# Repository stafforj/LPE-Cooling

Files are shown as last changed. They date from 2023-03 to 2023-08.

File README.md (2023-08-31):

# Liquid Exfoliation Cooling System

_A low-cost approach for cooling high shear exfoliation and material blending processes. The main cooling apparatus is constructed from 3D-printed components and off-the-shelf pipe connectors. Included are the designs and build notes. Part of the Open Science Framework repository [OpenLPE](https://osf.io/evupy/)._

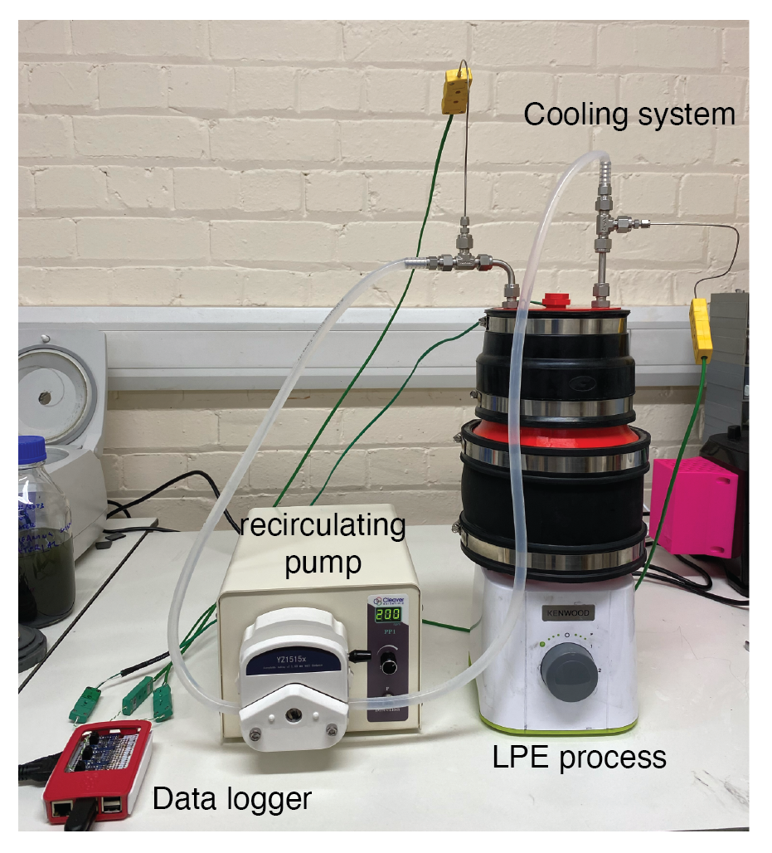
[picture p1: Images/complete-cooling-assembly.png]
Complete LPE assembly


## Background & Motivation

_This is part of the [OpenLPE](https://osf.io/evupy/) labware project._

High shear exfoliation is a process that uses mechanical force to produce atomically thin materials in liquid dispersions. Our research explores and utilises these processes to synthesise materials such as graphene, graphene-based materials, and others including transition metal dichalcogenides. We decided to create a low-cost, controllable shear exfoliation system that would be capable of synthesising reasonable product concentrations and formulating functional inks/composites at laboratory scales (~ 100 mL volumes). The aim was to design and build a scientific instrument which would allow researchers to do this with a low entry cost (~ 200 GBP). 

Standard kitchen blenders have previously been proven capable of performing high shear exfoliation of two-dimensional materials [[doi:10.1039/C4NR03560G](https://doi.org/10.1039/C4NR03560G), [doi:10.1016/j.carbon.2014.07.035](https://doi.org/10.1016/j.carbon.2014.07.035)]. Recently, our group has extended this accessible technique to include _in situ_ spectroscopy [[doi:10.1016/j.cherd.2021.10.041](https://doi.org/10.1016/j.cherd.2021.10.041)] and up-cycling of electric vehicle battery anodes at end-of-life [[doi:10.1021/acs.iecr.2c02634](https://doi.org/10.1021/acs.iecr.2c02634)]. High shear exfoliation processes tend to generate viscous heating which can increase product temperature significantly above ambient. For many applications and research investigations, it can be necessary to control these process temperatures (e.g., for chemical reactions or to avoid solvent evaporation).   

This repository provides the build details and CAD for creating a cooling system that can control the temperature of a liquid exfoliation process. These are designed around a high shear exfoliation process which utilises a controllable kitchen blender to impart a range of shear rates ($\dot{\gamma} \sim 10^2-10^5$ s $^{-1}$). We provide build details on how to modify and integrate programmable control of a kitchen blender here: [PID-Blender](https://github.com/DTP587/PID-Blender). Some of the CAD files are designed for this specific blender vessel (Kenwood BLP31.D0WG), however, the approach and configuration is extendable to any vessel and our CAD files and instructions can be used as templates to work from in these circumstances.

Below shows the recovery of few-layer graphene in aqueous-surfactant dispersions (De-ionised water / Sodium Cholate) that were produced using this cooled high shear exfoliation device.

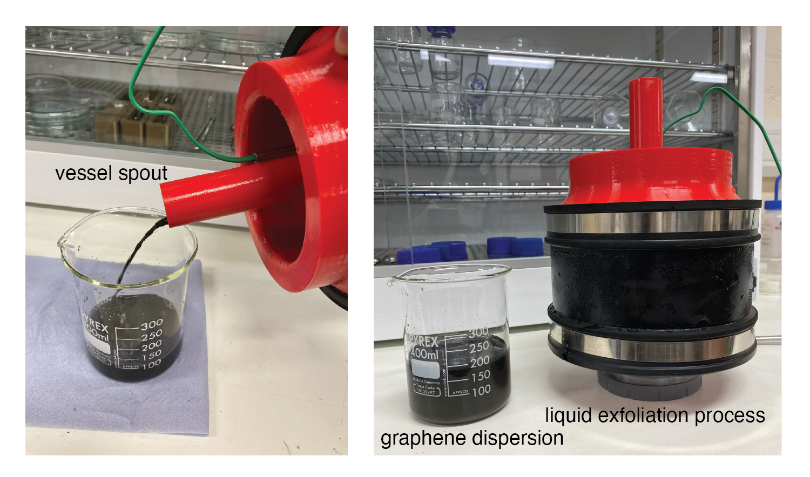
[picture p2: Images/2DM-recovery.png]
Production of FLG


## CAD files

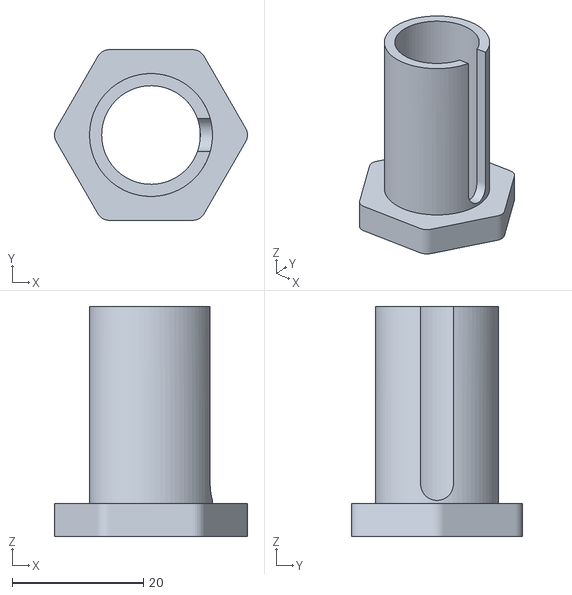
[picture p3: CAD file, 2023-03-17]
CAD/VesselCooler-TC-port.stl
29.4 x 26.0 x 35.0

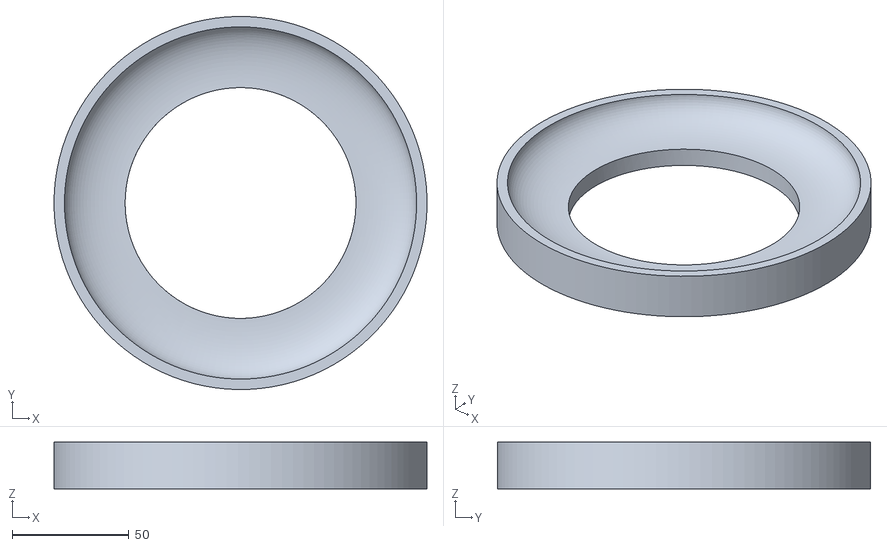
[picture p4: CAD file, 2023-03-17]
CAD/VesselCooler-Base.stl
160.0 x 160.0 x 20.0

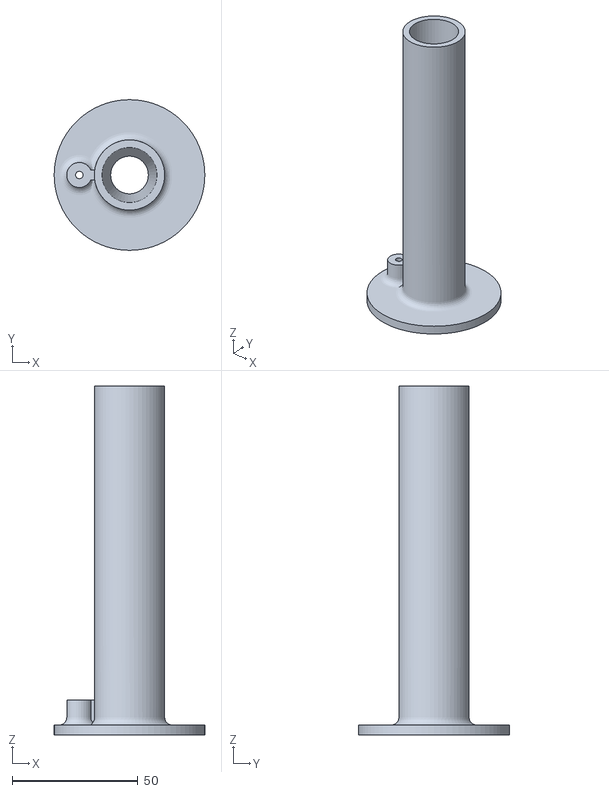
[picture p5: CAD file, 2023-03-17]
CAD/VesselCooler-chimney.stl
60.0 x 60.0 x 139.0

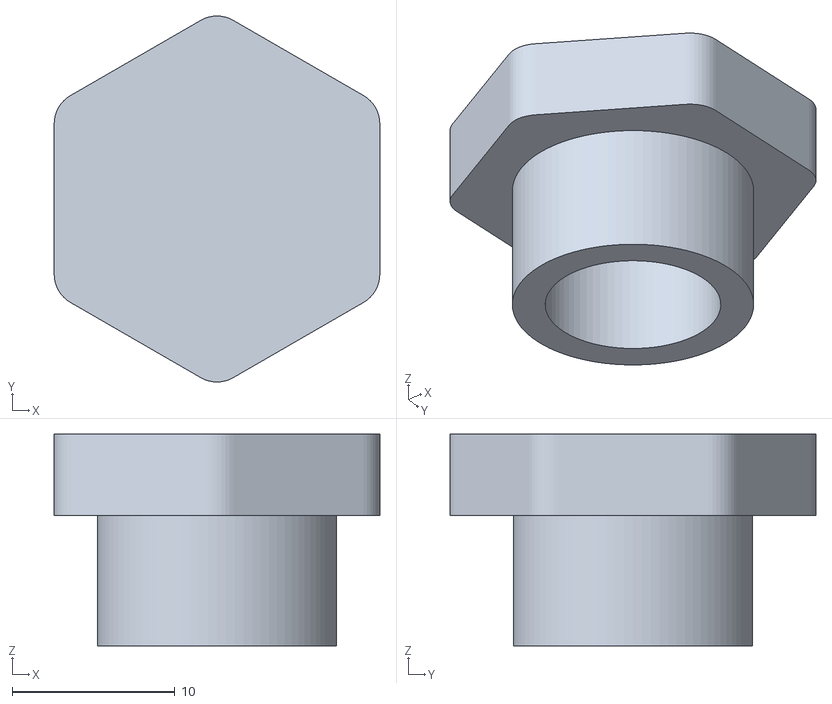
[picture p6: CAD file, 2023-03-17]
CAD/VesselCooler-TC-port-plug.stl
20.0 x 22.5 x 13.0

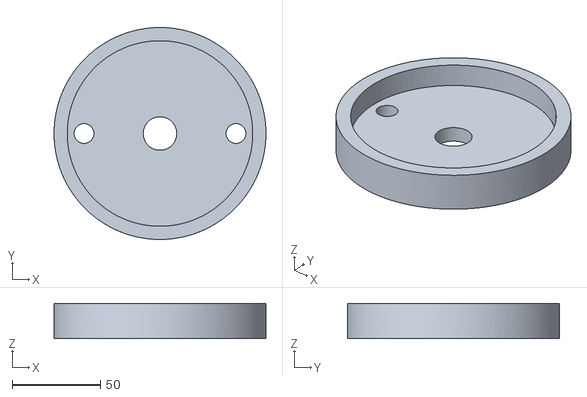
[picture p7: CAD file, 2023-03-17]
CAD/VesselCooler-Top.stl
120.0 x 120.0 x 20.0

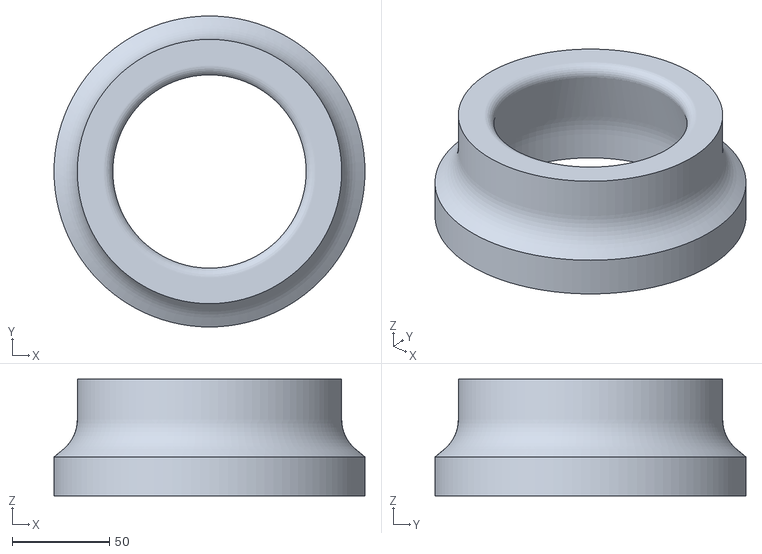
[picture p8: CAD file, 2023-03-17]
CAD/VesselCooler-Middle.stl
160.0 x 160.0 x 60.0

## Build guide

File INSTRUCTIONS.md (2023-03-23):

# Build Instructions and Notes

### Operating Principles

Liquid exfoliation processes, and many other mixing/formulation operations, impart high shear rates ($\dot{\gamma}$) on precursor materials dispersed in solvents. This action can generate heat through viscous heating of the fluid ($\dot{Q}$). A schematic of a liquid exfoliation process that uses a rapidly rotating impeller inside a closed vessel filled with solvent and precursor materials is shown in the schematic below. When the vessel is allowed to cool naturally in air, the amount of heat that can be dissipated from the system is limited by passive heat transfer modes from the external surface of the vessel to the ambient surroundings (natural convection & radiation, $Q_{nc}''$). This can result in uncontrollable and high product temperatures that can affect the mixing process if there is a sensitivity to temperature, and/or impact the reliability of the exfoliation system itself (thermo-mechanical failures).

The aim of this build is to provide a low-cost approach that can cool a kitchen blender vessel during the liquid exfoliation of nanomaterials. The operating principle of the cooling system is illustrated on the right in the schematic below. A cooling jacket surrounds the process vessel. The internal space is filled with ice cubes and chilled water which removes thermal energy from the process vessel using two heat transfer modes - the latent heat of fusion from a phase change of ice ($Q_{pc}''$) and the sensible heating of liquid water that is enhanced by coolant recirculation ($Q_{cv}''$).

This build can be combined with the following repositories to create a standalone, low-cost scientific apparatus with speed and temperature control: 

1. [Thermocouple-Datalogger](https://github.com/stafforj/Thermocouple-Datalogger) repository for temperature data aquisition module.
2. [PID-blender](https://github.com/DTP587/PID-Blender) repository for finely tuned blender speed control, or
3. [Automated-Relay-Switch](https://github.com/stafforj/Automated-Relay-Switch) repository for basic blender control.

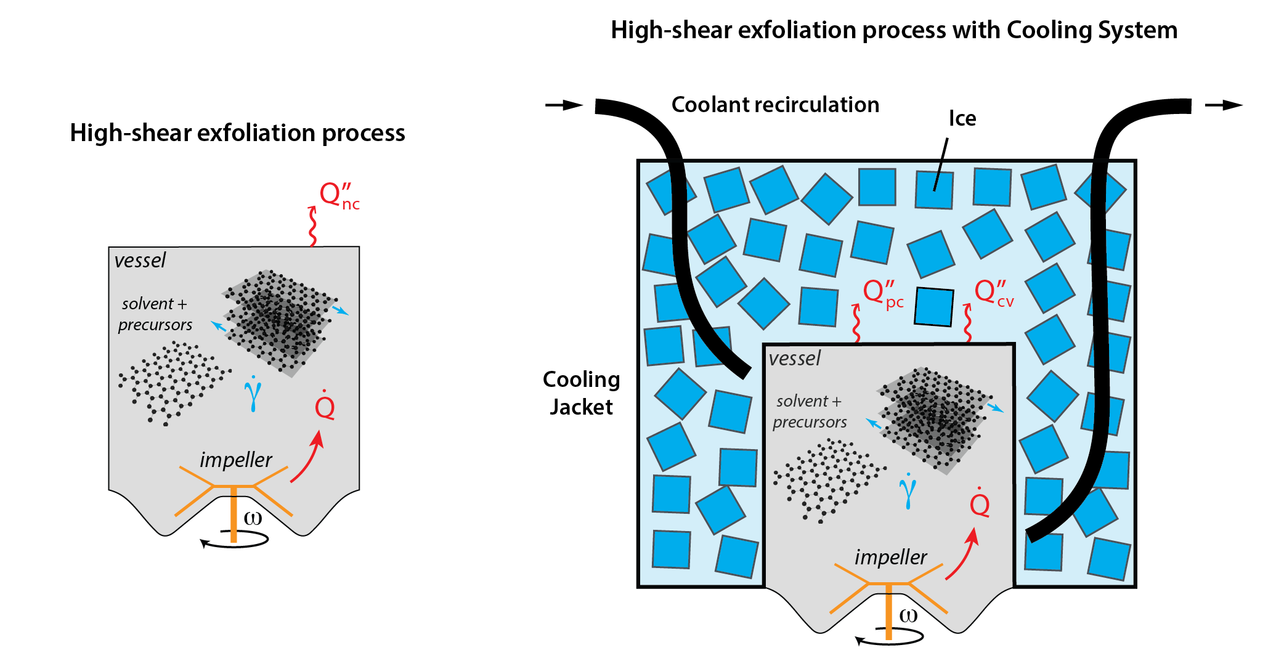
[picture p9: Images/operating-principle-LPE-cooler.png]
Operating principle


## Bill of Materials

The BoM is split into the main components for the cooling system and additional components that are optional. These additional parts facilitate coolant recirculation, or if using an external chiller to provide the cooling function instead of ice. The optional components listed below add greater cost to the build (relative to the main component costs). This cost can be reduced by moving to other types of fittings and tubing (e.g., brass fittings and copper tubing).

### Main items

|Name               |QTY|Description                           |
|:------------------|:-:|:-------------------------------------|
|PETG|1  |PETG filament for 3D-printing. 386 grams used to print all components. |
|[Silicon conformal sealant](https://uk.rs-online.com/web/p/conformal-coatings/1247695)|1 |Silicon conformal spray coating. Approximately 100 mL used.|
|[EPDM Pipe Adaptor (1)](https://www.screwfix.com/p/floplast-flexi-adaptor-160mm/1009v)|1  |Flexible EPDM pipe adaptor 160mm.|
|[EPDM Pipe Adaptor (2)](https://www.screwfix.com/p/floplast-underground-flexible-adaptor-120-136mm/19914)|1  |Flexible EPDM pipe adaptor 120-136mm.|
|[Adhesive/Sealant](https://www.screwfix.com/p/soudal-fix-all-high-tack-adhesive-sealant-white-290ml/64585)|1  |High bond strength adhesive/sealant. Approximately 30 mL used.|
|[Thermocouple](https://www.tcdirect.co.uk/product-2-190-1---Mineral-Insulated-Thermocouple-with-Pot-Seal-0-25-0-5-0-75-1-0-1-5-and-3-0mm-diameters)|1  |Type K thermocouple with 3 mm 310 SS probe sheath diameter, 100 mm length.|
|Bag of ice|1  |2 kg bag of ice cubes.|
|Thermocouple reader|1 |Data logger for reading Type K thermocouples. See our [Thermocouple-Datalogger](https://github.com/stafforj/Thermocouple-Datalogger) build for a RPi-based datalogger.
|Kitchen blender |1 |Standard off-the-shelf, [relay-controlled](https://github.com/stafforj/Automated-Relay-Switch), or [PID-controlled](https://github.com/DTP587/PID-Blender).
|[Funnel](https://www.fishersci.co.uk/shop/products/borosilicate-glass-powder-funnel-9/12993591?emb_id=pp_euorderconfirmation_producttitle) |1 |Glass/Plastic funnel for precursor loading. 70mm diameter (top), 16mm diameter (stem), 25 mm length.
|Misc.|   | <ul><li>Spanners</li><li>Screwdrivers</li><li>Gloves</li><li>Face mask</li><li>Electrical drill/Rotary tool</li><li>1L water</li></ul>|

### Coolant recirculation (optional)

|Name               |QTY|Description                           |
|:------------------|:-:|:-------------------------------------|
|SS tube|1  |1/4" stainless steel tube. 300mm length used. |
|[SS Bulkhead Union](https://buy.ham-let.com/774lss1-4)|2  |Bulk head fittings mounted to top 3D-printed part.|
|[SS Tube stub adapter](https://buy.ham-let.com/130ltss1-4x1-4)|2  |1/4" Hose barb fitting.|
|[SS Union Tee](https://buy.ham-let.com/764lss1-4)|2  |1/4" Tee fitting.|
|[SS Reducer](https://buy.ham-let.com/767ltss1-16x1-4tc)|2  |1/16" to 1/4" tube fitting.|
|[Thermocouple](https://uk.rs-online.com/web/p/thermocouples/3971501)|2  |Type K thermocouple with 1.5mm SS probe sheath diameter, 150mm length.|
|Tubing|1  |Silicon or Tygon tubing or similiar. 3m length used, 6mm or 1/4" ID. |
|Pump|1  |Pump of choice to recirculate coolant. |
|Misc.|   | <ul><li>Spanners</li><li>Screwdrivers</li><li>Pipe bender</li></ul>|

## Design & Construction

### Thermal Design

The hardware design is based on the thermal loads that need to be dissipated from the liquid exfoliation system. For this build we use a 350 W Kenwood BLP31.D0WG blender. We typically operate the process for $t ≈ 15$ mins to perform a synthesis [[doi:10.1021/acs.iecr.2c02634](https://doi.org/10.1021/acs.iecr.2c02634)]. Next, we can estimate the amount of ice that would melt into liquid water using the latent heat of fusion.

```
Heat load: 350 W = 350 J/s = 21 kJ/min
Latent heat of fusion = 334 kJ/kg

21kJ/min / 334kJ/kg = 0.063 kg/min
1260kJ/h / 334kJ/kg = 3.77 kg/h
```
Which shows that ≈ 1 kg of ice can melt in 15 mins. This is a basic starting point for sizing the cooling jacket. For this application, the design must be capable of holding 1 kg of ice around the vessel at a minimum. Ideally, it should be made bigger than this to accommodate the simplified assumptions that have been made, secondary heat loss/gain, as well as accounting for any future requirements such as longer process times.

Adding ice cubes to the cooling jacket leaves air gaps that have a negligible contribution to the heat transfer from the vessel. The complete surface of the heated process vessel also won't be in direct contact with the ice due to these voids. Filling and recirculating chilled water (e.g., $T$ ≈ 0.1-1°C) can remove these insulative air gaps with a liquid coolant and promote uniform cooling over the entire vessel surface (see previous schematic). If the jacket is filled with an additional 1 L of chilled water, the sensible heating contribution assuming a target temperature rise of 10°C can be calculated as:

```
m: mass of chilled water (1kg) + mass of melt water (1kg)
Cp: specific heat capacity
DT: temperature rise

Q_s = m*Cp*DT = 2*4184*10 = 83.7 kJ
```

Although this is a useful cooling contribution, it also illustrates the importance of phase change heat transfer to the cooling process (recall the value for latent heat of fusion). A jacket size of 2.6 L was chosen to meet the material processing requirements. This provided a volume ≈ 25% greater than the 2.1 L that this simple analysis was based on (1kg ice + 1L water).

Additionally, as the jacket temperature is lower than the ambient air outside ($T_{amb}$ ≈ 20°C in the lab), heat is gained by the cooling system. We can calculate this assuming a heat transfer coefficient of $h = 7.5$ W/m $^2$ K, representing an average of the typical range of $h$ for natural convection (~ 5-10 W/m $^2$ K). Taking a cooling jacket diameter of 170 mm and height of 250 mm, the heat gained from the ambient, $Q_g$ is:

```
h: heat transfer coefficient
A: external surface area of the cooling jacket
DT: temperature difference between the ambient air and cooling jacket

Q_g = h*A*DT = 7.5*(2*pi*0.085*0.250)*20 = 20 W
20 W = 20 J/s =  1.2 kJ/min
```
This assumes the external surface is not insulated. Wrapping the cooling jacket with insulation can reduce some of the heat gain to the jacket. The final estimates accounting for $Q_s$ and $Q_g$ are:

```
Energy from latent heat of fusion: 334 kJ
Energy from heating 2 kg water by 10°C: 83.7 kJ
Total energy = 417.7 kJ to heat the ice/water jacket mixture by 10°C

Heat generation from LPE process: 21 kJ/min
Ambient heat gain: 1.2 kJ/min
Total heat rate = 22.2 kJ/min (heat added to ice/water jacket)

Total processing time before the coolant temperature reaches 10°C
t = 417.7 / 22.2 = 18.8 min
```
This provides sufficient flexibility to facilitate cooling for a target process time of $t = 15$ mins. Note that this only considers heat loads during the process "ON" time. If the process is run intermittently (e.g., 1 minute ON, 1 minute OFF, etc.), the ambient heat gain persists during the process OFF time. A revised estimate of the cooling time should be calculated with these considerations.

### CAD files

A total of six components from the cooling system are 3D-printed parts. The CAD (.stl) files for printing these parts are located within the folder `./CAD/`.

### Construction

The CAD files were printed using a fused-deposition-modeling (FDM) printer (Ultimaker S3, 0.2mm layer thickness, 20\% infill, no supports). Polyethylene terephthalate glycol (PETG) was selected as the filament material for the printing process due to its ability to tolerate high temperatures (~ 70-80°C), its mechanical properties, printability, and chemical resistance to certain oils and solvents. 

In this build, the components are exposed to water and ice. Although PETG is compatible with water, the layers resulting from the FDM process can create sites for fluid leakages in the finished part. To remove the risk of leaks, the 3D-printed parts were coated with a thin film silicon-based conformal coating (~ 100 microns thickness). To show the visual effect of this coating, a sample part was 3D-printed and masked with tape to partially cover it with a single spray coat (~ 25 microns). The difference between the coated and uncoated PETG surface is shown in the image below. The conformal coating covers the layers and insterstices, sealing the printed part and preventing liquid leaks. This surface coating is mechanically robust. As the surfaces in contact with the coolant and product are a different material than PETG, the chemical resistance of coated parts should be re-assessed for applications where a coolant other than water/ice is used. The spray coating should be performed in a well-ventilated environment and wearing the appropriate PPE.   

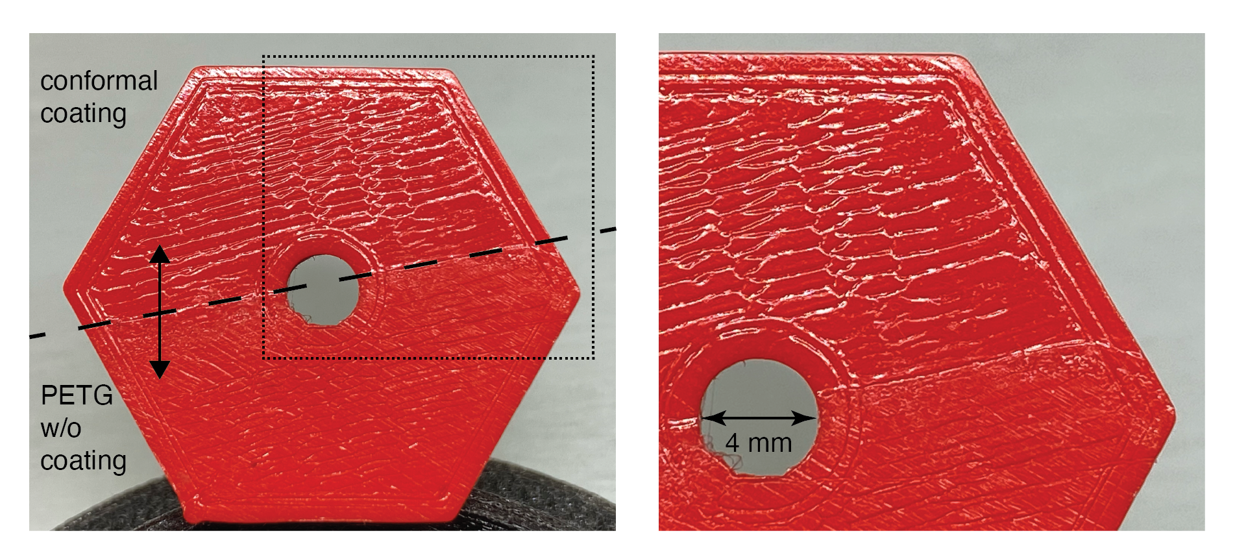
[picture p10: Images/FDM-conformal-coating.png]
Conformal coating


Once printed, the parts were coated with three spray coats and allowed to cure at room temperature (~ 20°C) for 24 hours between coatings. The components of the cooling system are shown in the image below.

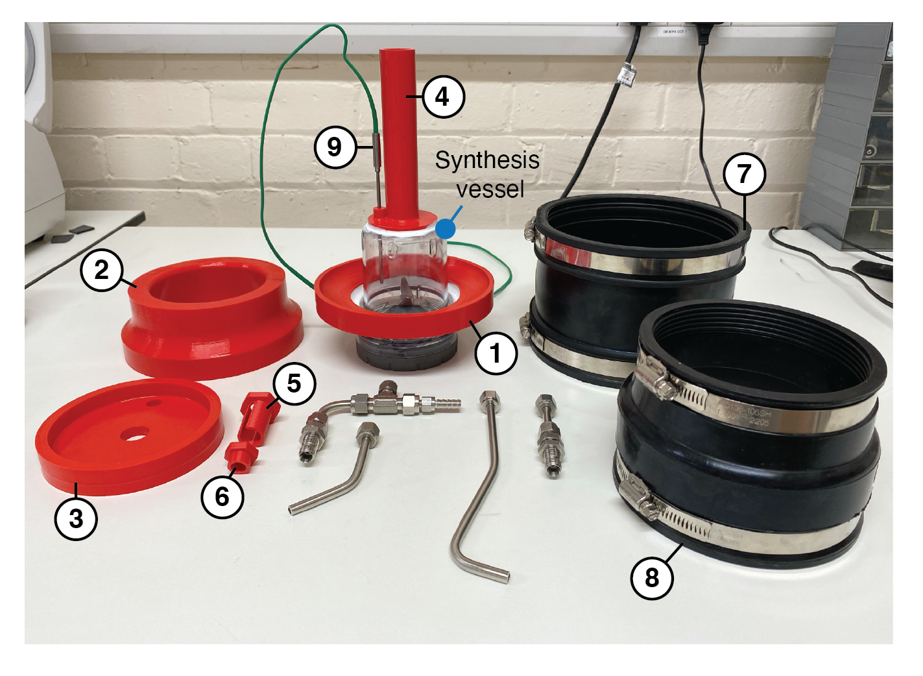
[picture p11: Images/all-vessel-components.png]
Component breakdown


Components `1`, `4` and `9` were bonded to the synthesis vessel (Kenwood BLP31.D0WG) using a sealant adhesive. The spout with integrated thermocouple mounting (Component `4`), required modifications to the synthesis vessel before the bonding process. A 15 mm diameter hole was drilled at the top and centre of the vessel. This hole allows filling the vessel with precursor materials from the top (shown later). A second 4 mm diameter hole, located 20 mm from the centre of the vessel, was drilled to accomodate the insertion of a thermocouple probe for measuring the process temperature. The thermocouple probe is inserted into component `4` at the desired depth, and the part then bonded to the top of the vessel. 

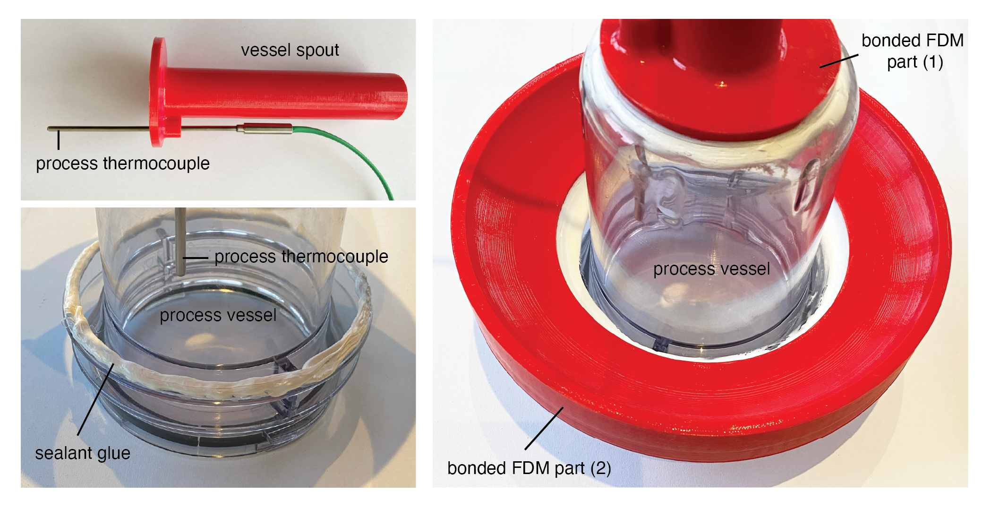
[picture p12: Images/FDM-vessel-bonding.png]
Bonding construction


The complete assembly instructions are discussed in the following sections. The following image shows the barebone assembly of printed parts and synthesis vessel without the cooling jacket installed. The vessel spout was also designed to facilitate product sampling during material processing. Here, you can see a 10 mL pipette inserted into the vessel through the opening in the top part. Product samples can be taken without dissassembling the vessel, or interfering with the thermocouple or cooling system itself. The (optional) coolant recirculation pipes were formed using SS tubing and a pipe bender. These are intended to transport cooling fluid onto and away from the synthesis vessel, improving the convective heat transport from the external walls of the vessel ($Q_{cv}"$).        

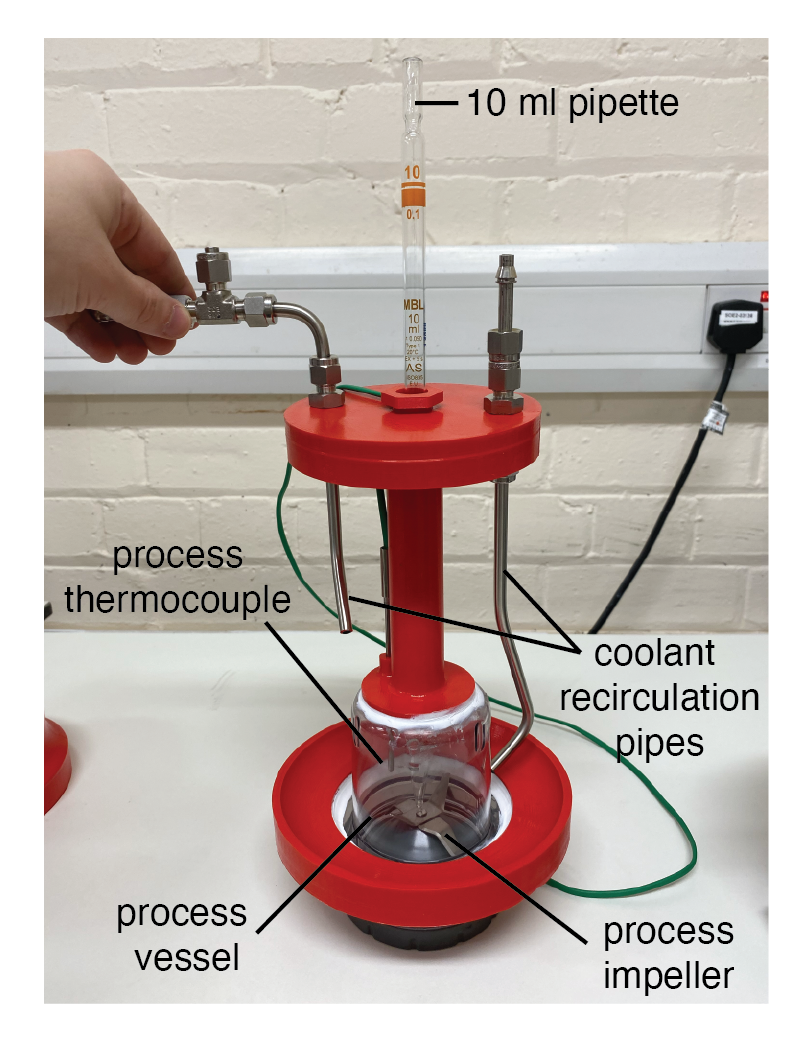
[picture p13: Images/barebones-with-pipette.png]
Barebones without EPDM cylinders


## Assembly of Liquid Exfoliation Cooling System 

### Steps 1-4: Cooling jacket assembly

1. Connect the lower cylinder to the base of the synthesis vessel. Tighten the lower hose clip to secure the EPDM pipe connector (component `7`) in place.
2. Insert the mid-section part (component `2` in the part breakdown shown above) and tighten the second hose clip.
3. Connect the upper cylinder to the mid-section (component `2`) and tighten the lower hose clip of this EPDM pipe connector (component `8`) to secure it.
4. Guide the thermocouple connector and cable (component `9`) through the central hole. Do not secure the top part in the EPDM pipe connector (component `8`) at this stage. If using an external pumped cooling loop, mount the coolant recirculation pipes and pipe connectors to the top part (component `3`). 

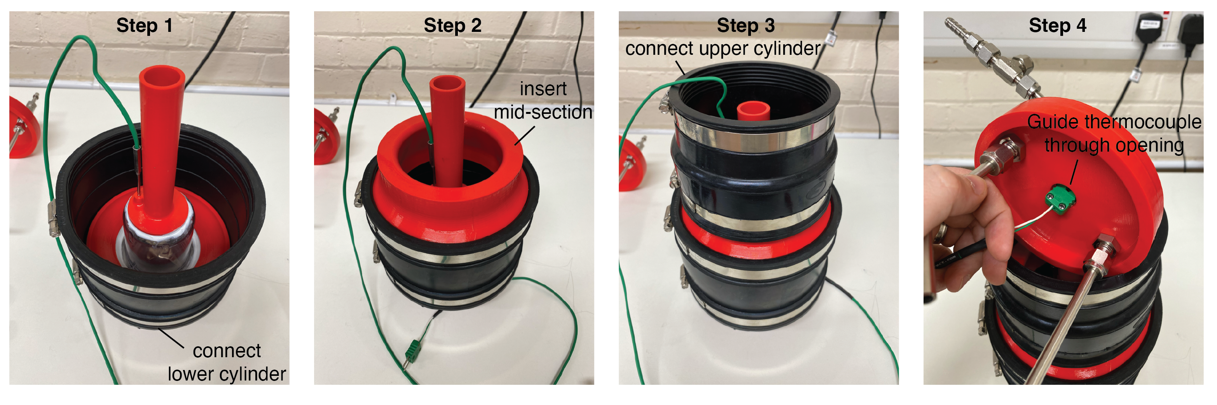
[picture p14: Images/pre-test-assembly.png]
Assembling jacket


### Step 5: Precursor filling

5. Insert a funnel into the top of the spout (component `4`) and load the solvent and precursor materials into the mixing vessel.

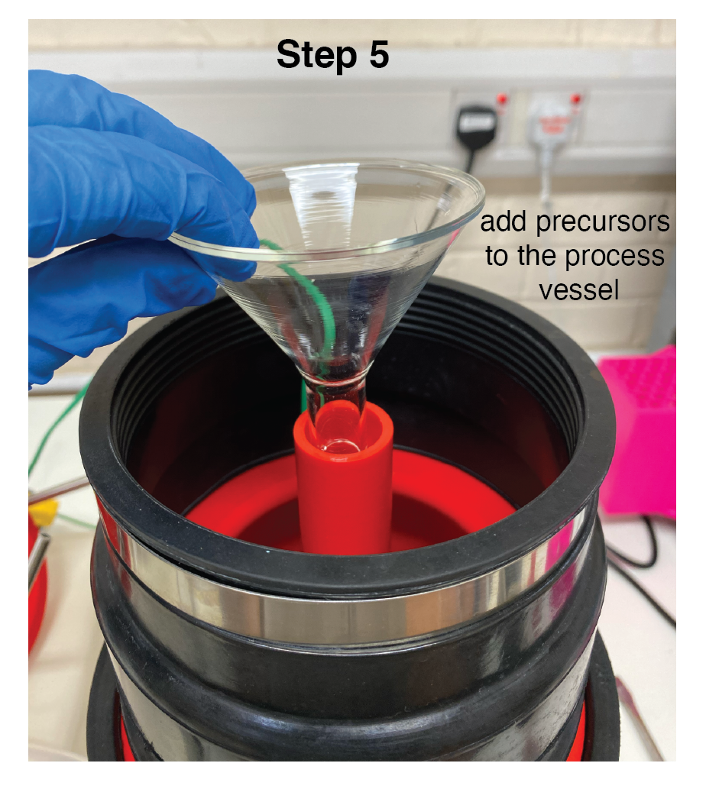
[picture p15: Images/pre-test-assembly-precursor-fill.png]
Fill internal vessel


### Step 6: Ice filling

6. Pack the cooling jacket with ice cubes. Note: the size of the ice cubes impacts how much can be added. If a maximum ice fill is required (≈ 2 kg), the kitchen blender can also be used to break up large ice cubes into smaller pieces that can pack into the cooling jacket with less voids. 

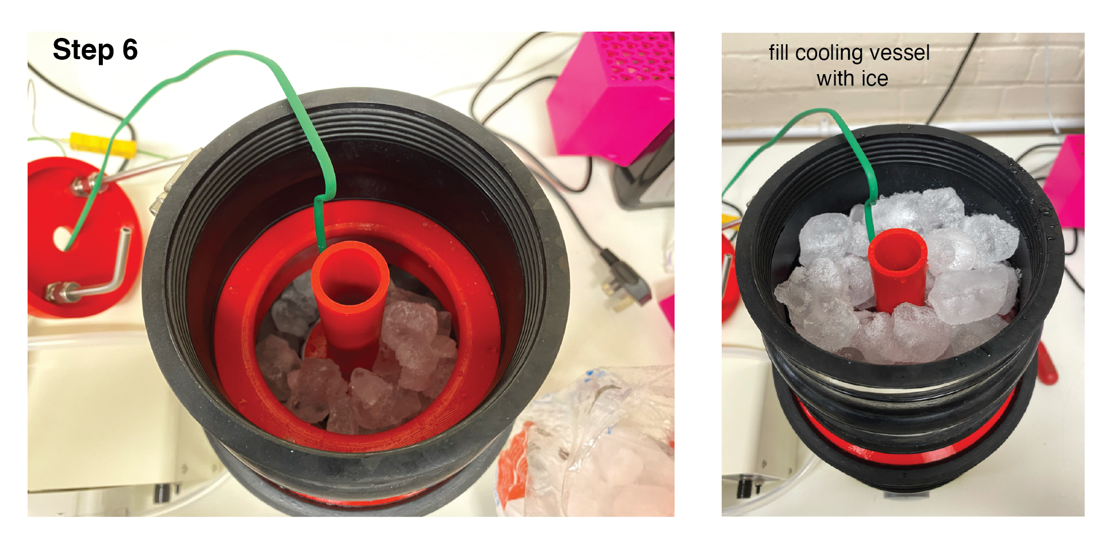
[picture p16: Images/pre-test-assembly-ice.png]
Ice packing


### Step 7: Cooling jacket closure

7. Insert the top section (component `3`) and tighten the second hose clip on the EPDM pipe connector (component `8`) to secure and seal the cooling jacket. If using an external pumped cooling loop, connection the pump tubes for coolant circulation.

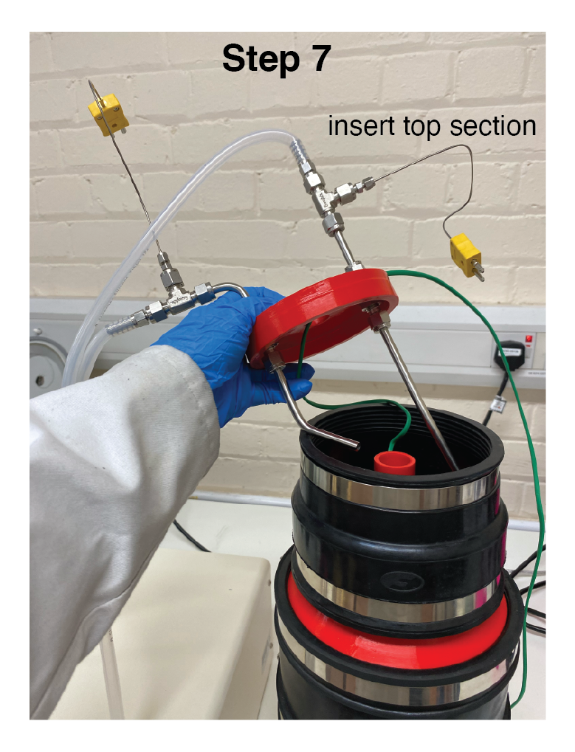
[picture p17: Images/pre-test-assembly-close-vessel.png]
Top insertion


### Step 8-9: Thermocouple routing 

8. Fit the thermocouple port insert (component `5`) into the top section (component `3`), guiding the thermocouple cable through the slot. Push fully into place as shown in the images below. This component fits through the top section and into the vessel spout.
9. Insert the thermocouple port plug (component `6`) to close the opening to the vessel spout. This can be removed during product sampling and re-inserted.

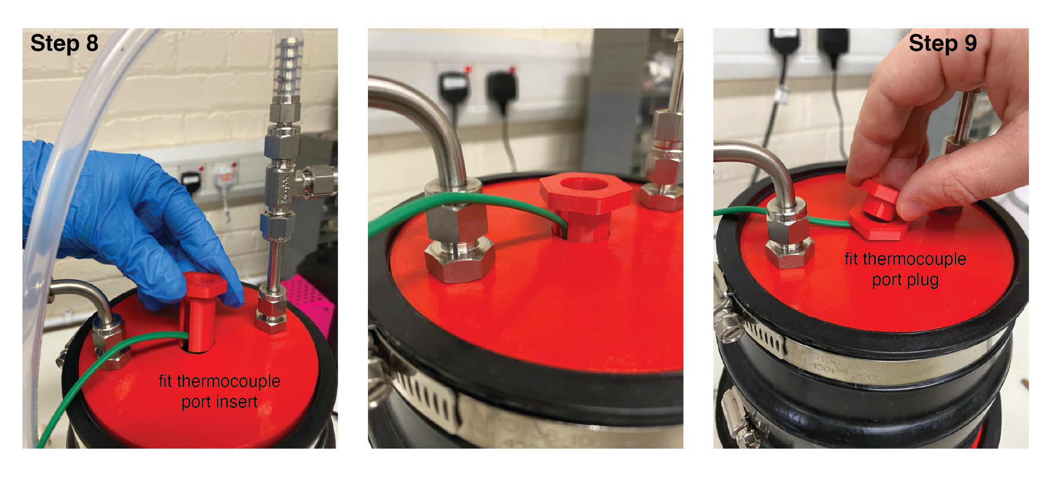
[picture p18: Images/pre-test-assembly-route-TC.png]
TC plugging


### Step 10: Connecting to thermocouple datalogger

10. Connect the process thermocouple to the data logger. If using an external pumped cooling loop, with additional coolant thermcouples on the inlet and outlet, connect these to the data logger also.

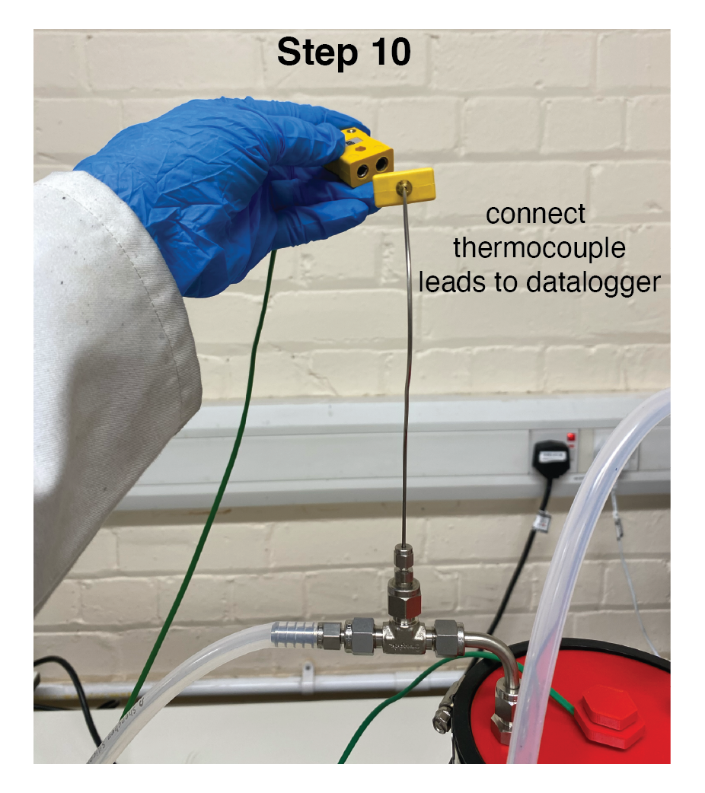
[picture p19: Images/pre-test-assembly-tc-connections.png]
TC connections


This completes the cooling system assembly for the liquid phase exfoliation (LPE) process.

Completed installation

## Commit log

2023-03-17 cad files
    [VesselCooler-Base.stl, VesselCooler-Middle.stl, VesselCooler-TC-port-plug.stl, VesselCooler-TC-port.stl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]
2023-03-17 complete assembly
2023-03-22 assembly instructions
